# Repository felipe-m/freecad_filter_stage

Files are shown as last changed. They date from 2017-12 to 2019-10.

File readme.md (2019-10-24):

# One-axis stage to move a filter

This is a parametrizable open-source hardware (OSH) stage to move an optical filter. 
The dimensions of the filter and the stage are parametrizable in order to change the dimensions of the stage, the filter and any other components (stepper motor, belt tensioner, aluminum profiles,..)
The printable pieces are described using [FreeCAD](http://freecadweb.org/) Python scripts.
It can be compared with the OpenSCAD version: https://github.com/felipe-m/oscad_filter_stage

1. [License](#license)
2. [Description](#description)
3. [Assembly](#assembly)
4. [Main parameters](#main_parameters)
    1. [Filter Holder Parameters](#filter_holder_param)
    2. [Belt Tensioner](#belt_tensioner_param)
5.  [Project organization](#directory)
6.  [Printable Parts](#printed_parts)
    1. [Parts with step by step tutorial](#tutorial_step)
    2. [The rest of the parts](#no_tutorial)
7.  [Print settings](#print_set)

**The pictures of this readme.md are reduced in size to make the document more readable** larger pictures can be found in the img folder (see [Project organization](#directory))

---
## License 

Hardware License: CERN 1.2 (https://ohwr.org/cernohl)

Software License: [LGPL 3.0](./License.md)

Documentation License: CC BY 4.0 (https://creativecommons.org/licenses/by/4.0/)

ES000004

This project has been certified as [open source hardware](https://certification.oshwa.org/es000004.html) by the [Open Source Hardware Association](https://www.oshwa.org/). 

## Description 

The components of the stage are:
* Filter holder
* Timming belt
* Belt tensioner
* Stepper motor with pulley
* Motor holder
* Linear guide
* Some nuts and bolts

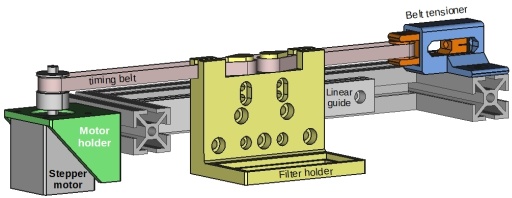
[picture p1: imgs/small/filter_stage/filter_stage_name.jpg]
Filter Stage Names


---

## Assembly 

### Filter holder

The filter holder holds an optical filter and it is attached to a linear guide. 

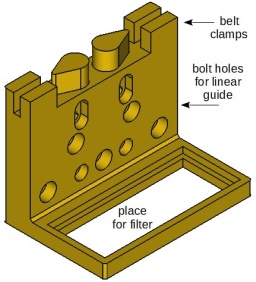
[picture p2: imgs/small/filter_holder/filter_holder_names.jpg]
Filter Holder Names


It has various holes to be able to fit in different linear guides

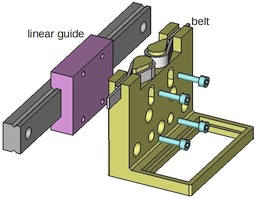
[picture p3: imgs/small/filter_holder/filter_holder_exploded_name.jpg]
Filter Holder Exploded


### Belt tensioner

The belt tensioner is composed by 2 printable parts, and idler pulley:
* Tensioner holder
* Idler tensioner
* Idler pulley
* Leadscrew with nut

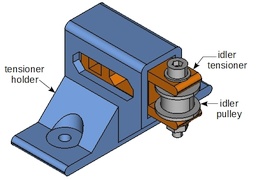
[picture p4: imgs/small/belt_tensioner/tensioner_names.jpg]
Belt tensioner front


Back view of the belt tensioner:

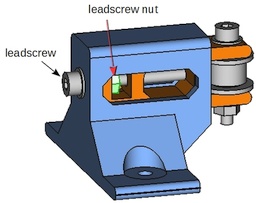
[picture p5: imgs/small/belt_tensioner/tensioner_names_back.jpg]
Belt tensioner back


Exploded view of the belt tensioner:

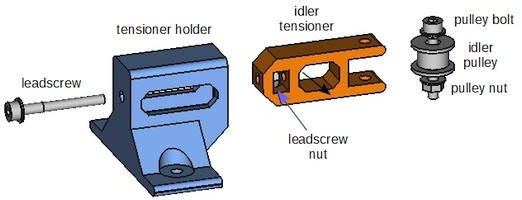
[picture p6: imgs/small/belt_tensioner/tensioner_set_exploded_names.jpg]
Belt tensioner exploded


By turning the leadscrew, the idler pulley will retract or extend, tightening or loosening the belt. 

Retracted belt tensioner:

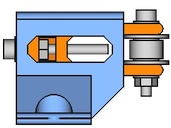
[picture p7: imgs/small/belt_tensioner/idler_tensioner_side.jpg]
Belt tensioner retracted


Extended belt tensioner:

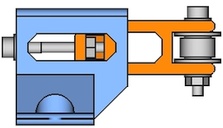
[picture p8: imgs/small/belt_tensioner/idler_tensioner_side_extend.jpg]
Belt tensioner extended


The idler pulley can be made out of a bearing, a bolt, a nut and some washers. 
For example, if using a DIN 912 bolt, it can be built this way:

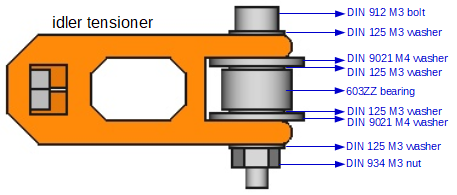
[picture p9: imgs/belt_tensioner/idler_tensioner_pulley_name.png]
Idler pulley bearing


---

## Main Parameters 
Following, the main parameters are explained.
There are some other parameters that can be seen in the Python code.

---

### Filter Holder Parameters 

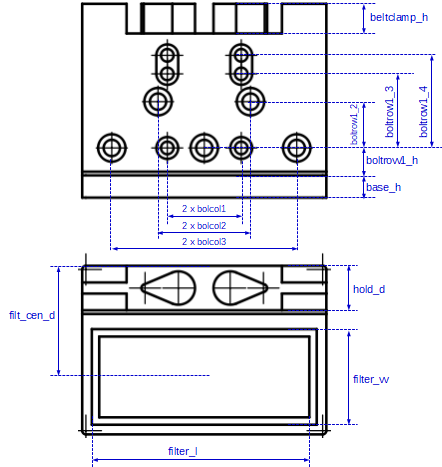
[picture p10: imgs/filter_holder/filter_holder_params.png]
Filter holder parameters


Example of 2 filter holders having different parameters:

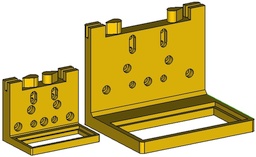
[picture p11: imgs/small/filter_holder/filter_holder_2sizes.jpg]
2 Filter holder size


---

### Belt tensioner Parameters 

Idler tensioner size depending on the idler pulley:

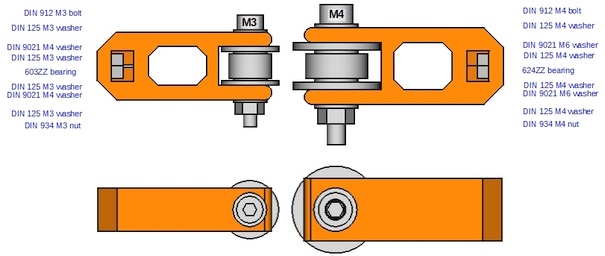
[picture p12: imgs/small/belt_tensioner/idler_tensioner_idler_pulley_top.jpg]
Idler tensioner size depending on the idler pulley


---

The tensioner stroke can be modified:

tensioner stroke

---

The thickness of the walls can be modified

tensioner wall thick

---

The metric size of the leadscrew can be modified:

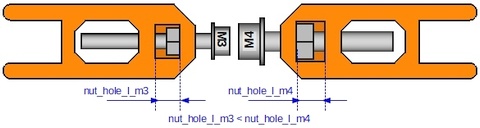
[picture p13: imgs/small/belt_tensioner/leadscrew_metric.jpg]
Leadscrew size


---

These modifications lead to automatic modifications on the tensioner holder size:

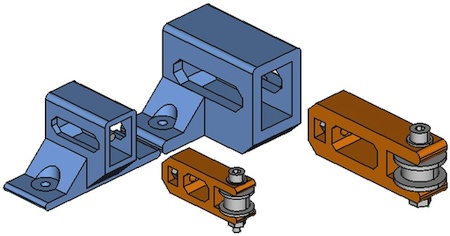
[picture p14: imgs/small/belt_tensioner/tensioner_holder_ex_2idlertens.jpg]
Tensioner holder size


---

The belt height is parametrizable, leading to modifications on the tensioner holder:

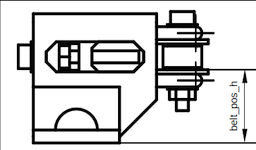
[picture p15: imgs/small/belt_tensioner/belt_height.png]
Belt height


---

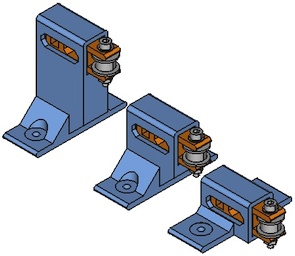
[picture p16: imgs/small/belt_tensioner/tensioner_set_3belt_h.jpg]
Belt height


---

The base width, ie. the aluminum profile width, is parametrizable:

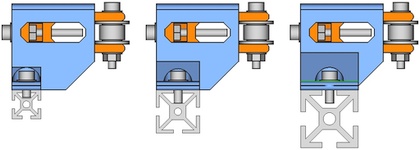
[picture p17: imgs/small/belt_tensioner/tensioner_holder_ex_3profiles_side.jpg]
Base width


---

## Project organization 
```
 +--- scr: Source files in Python
    +--- comps: functions in Python for FreeCAD, https://github.com/felipe-m/fcad-comps
 +--- scr_cq: Source files in Python using CadQuery   
 +--- freecad: Saved FreeCAD designs
 +--- stl: Parts exported to STL
 +--- imgs: Images of the 4 parts in png format
    +--- small: reduced size images
    +--- tens_hold_steps: images for the step by step explanation for the tensioer holder
    +--- idler_tens_steps: images for the step by step explanation for the idler tensioner
    +--- belt_tensioner: belt tensioner images
    +--- filter_holder: filter holder images
    +--- filter_stage: filter stage images
```

 comps: are python functions and classes to make the shapes easier. Check https://github.com/felipe-m/fcad-comps

---

## Step by step explanations :

### Step by step explanations :

1. [tensioner_holder.md](./tensioner_holder.md) Detailed explanation for the tensioner holder. It also includes information on how to execute the Python scripts. 
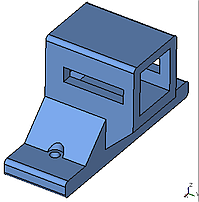
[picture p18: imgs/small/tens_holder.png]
Tensioner Holder

1. [idler_tensioner.md](./idler_tensioner.md) Detailed explanation for the idler tensioner
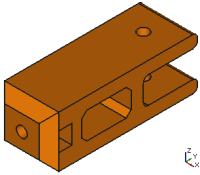
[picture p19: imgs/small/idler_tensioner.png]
Idler Tensioner


You can compare the same pieces designed using OpenSCAD: https://github.com/felipe-m/oscad_filter_stage

---

### Designs with no step by step explanations :
1. The [tensioner_set.py](src/tensioner_set.py) module has no detailed explanation, but the code is explained based on the previous. This code combines the parts of the tensioner set and uses Python classes and methods.
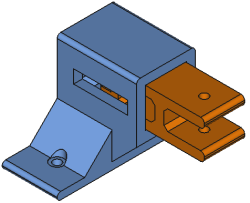
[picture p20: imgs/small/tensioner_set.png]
Tensioner Set

1. [filter_holder_clss.py](src/filter_holder_clss.py) Filter holder, similar to the one made with OpenSCAD (https://github.com/felipe-m/oscad_filter_stage)
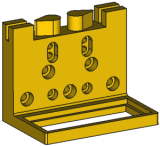
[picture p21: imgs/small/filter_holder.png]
Filter Holder

1. [filter_stage.py](src/filter_stage.py) In the same design includes the filter holder, the belt tensioner and the motor holder, and also some other non-printable models, such as the stepper motor, aluminum profile, linear guide, belt and pulleys
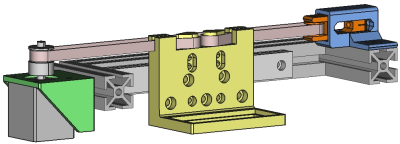
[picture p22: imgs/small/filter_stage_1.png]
Filter Stage

1. CadQuery designs have no step-by-step explanations, but there are comments in the code:
 + [cq_idler_tensioner.py](src_cq/cq_idler_tensioner.py)
 + [cq_tensioner_holder.py](src_cq/cq_tensioner_holder.py)
 + [cq_nemamotor_bracket.py](src_cq/cq_nemamotor_bracket.py)
 + [cq_filter_holder.py](src_cq/cq_filter_holder.py)
 
## Print settings :

There is no need to have supports as long as the parts are printed with the following orientation:

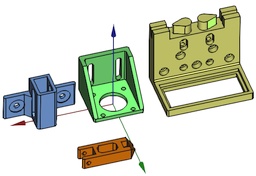
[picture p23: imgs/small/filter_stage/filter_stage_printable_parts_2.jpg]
Print orientation


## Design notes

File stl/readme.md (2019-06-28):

* [idler_tensioner.stl](idler_tensioner.stl) is the result of [idler_tensioner.py](../src/idler_tensioner.py)
* [tensioner_holder.stl](tensioner_holder.stl) is the result of [tensioner_holder.py](../src/tensioner_holder.py)
* [set_idler_tensioner.stl](set_idler_tensioner.stl) and [set_tensioner_holder.stl](set_tensioner_holder.stl) are the result of [tensioner_set.py](../src/tensioner_set.py)
* [class_idler_tensioner.stl](class_idler_tensioner.stl) and [class_tensioner_holder.stl](class_tensioner_holder.stl) are the result of [tensioner_clss.py](../src/tensioner_clss.py) used in the [filter stage example](../src/filter_stage.py).
* [filter_holder.stl](filter_holder.stl) is the result of [filter_holder_clss.py](../src/filter_holder_clss_clss.py) used in the [filter stage example](../src/filter_stage.py).
* [motor_holder.stl](motor_holder.stl) is a part of the same [filter stage example](../src/filter_stage.py).

---

## Print orientation

This sample parts are from the [filter stage example](../src/filter_stage.py).

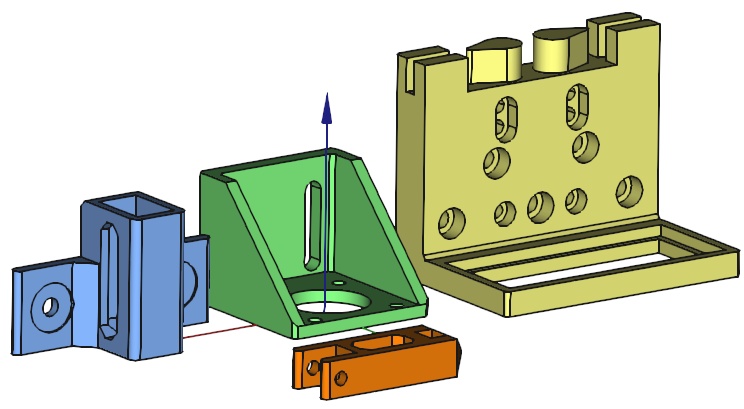
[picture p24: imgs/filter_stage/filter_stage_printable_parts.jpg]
Print orientation


---

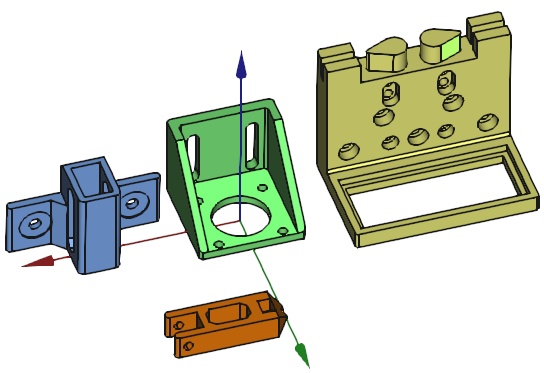
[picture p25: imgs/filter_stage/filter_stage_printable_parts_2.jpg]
Print orientation 2


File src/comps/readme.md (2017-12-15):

# FreeCAD scripted components and functions

## `kcomp.py`

Constants and dimensions for components:
* LME10UU, LME12UU linear bearing
* E3D V6 extruder
* DIN-912 bolt
* DIN-934 nut
* SK12 shaft holder

It also includes the default tolerances and the 3D printer layer height

## `comps.py`

Creates freecad components

### Dependencies:
../fcfun functions
/../../freecad/comps/misumi_profile_hfs_serie6_w8_30x30.FCStd

### Components

**class Sk**

SK12 shaft holder

**class MisumiAlu30s6w8**

Misumi Aluminum extrusion 30x30 hfs serie 6 width 8

## `fcfunc.py`

Python functions and constants for FreeCAD scripts

```
def addBox (x, y, z, name, cx= False, cy=False)
def addCyl (r, h, name)
def addBolt (r_shank, l_bolt, r_head, l_head,
             hex_head = 0, extra=1, support=1, headdown = 1, name="bolt")
def addBoltNut_hole (r_shank,        l_bolt, 
                     r_head,         l_head,
                     r_nut,          l_nut,
                     hex_head = 0,   extra=1,
                     supp_head=1,    supp_nut=1,
                     headdown=1,     name="bolt")         
class NutHole ()
    def __init__(self, nut_r, nut_h, hole_h, name,
                 extra = 1, nuthole_x = 1, cx=0, cy=0, holedown = 0)            
def fillet_len (box, e_len, radius, name)            
```

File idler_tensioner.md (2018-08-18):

# FreeCAD python scripts detailed steps for the Idler Tensioner

Idler Tensioner

This example is created using python functions defined in the folder src/comps

The source file: [idler_tensioner.py](src/idler_tensioner.py)

The resulting FreeCAD model: [idler_tensioner.FCStd](freecad/idler_tensioner.FCStd)

This tutorial can be compared with the [OpenSCAD tutorial](https://github.com/felipe-m/oscad_filter_stage) for this [Idler Tensioner](https://github.com/felipe-m/oscad_filter_stage/blob/master/idler_tensioner.md) 

With FreeCAD you can navigate through the model:

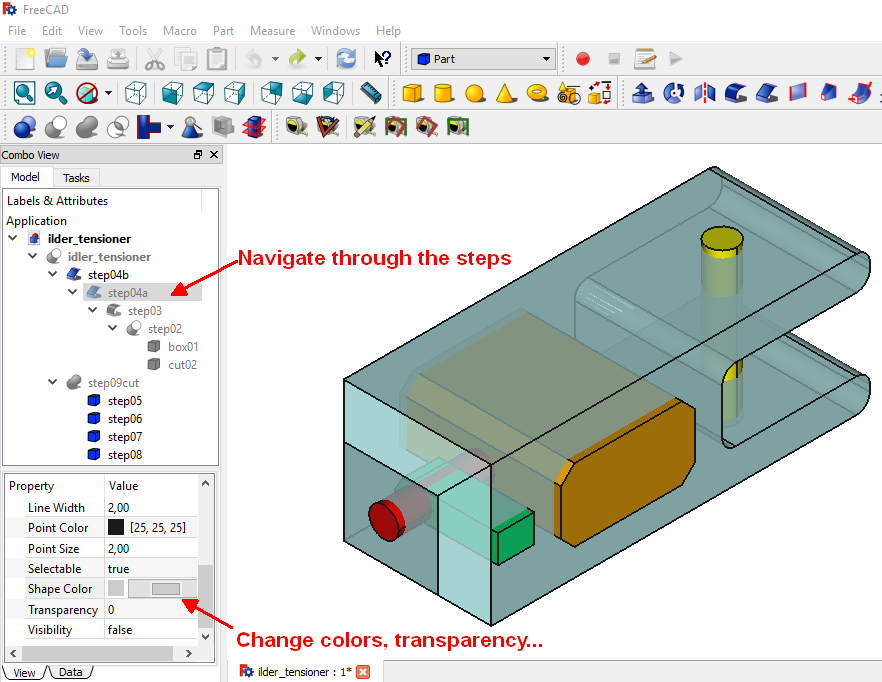
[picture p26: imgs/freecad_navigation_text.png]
Navigate


You may want to check the steps for the [tensioner holder](./tensioner_holder.md), which have been also created using Python scripts, but using other kind of functions

Back to the [readme.md](./readme.md)

# Steps

## Step 00: Libraries import and function creation

```python
import os
import sys
import FreeCAD
import FreeCADGui
import Part

# to get the current directory. Freecad has to be executed from the same
# directory this file is
filepath = os.getcwd()
# to get the components
# In FreeCAD can be added: Preferences->General->Macro->Macro path
sys.path.append(filepath) 
#sys.path.append(filepath + '/' + 'comps')
sys.path.append(filepath + '/../../' + 'comps')

import kcomp   # import material constants and other constants
import fcfun   # import my functions for freecad. FreeCad Functions
import comps   # import my CAD components
import partgroup   # import my CAD components
import kidler  # import constants for the idler tensioner and holder
import kparts

def idler_tens ():
    # bring the active document
    doc = FreeCAD.ActiveDocument
```

## Step 01: Create the box
Everything else will cut the box:

```python
    #  --------------- step 01 ---------------------------      
    #  rectangular cuboid with basic dimensions
    # 
    #           Z
    #           :.....tens_l.......
    #           :_________________:
    #           /                /|
    #          /                / |
    #       ../________________/  |..............Y     .
    #      :  |                |  /     . 
    # tens_h  |                | /     . tens_w
    #       :.|________________|/......
    #        .
    #       .
    #      X 
    #
    # oscad: cube([tens_w, tens_l, tens_h]);

    # creates the shape, you don't see it yet on FreeCAD Gui
    shp01 = fcfun.shp_boxcen(kidler.tens_w, kidler.tens_l, kidler.tens_h)
    # creates a freecad object from the shape, to see it in FreeCAD Gui,
    # not necessary, but illustrative for this tutorial
    fcd01 = fcfun.add_fcobj(shp01, 'box01')

```

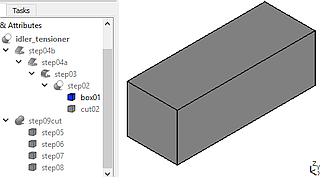
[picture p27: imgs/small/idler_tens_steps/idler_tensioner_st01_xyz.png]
Step 01


## Step 02: Space for the idler pulley

```python
    #  --------------- step 02 ---------------------------  
    # Space for the idler pulley
    #      Z
    #      :
    #      :_______________________
    #      |                 ______|....
    #      |                /          + idler_h
    #      |               |           :
    #      |                \______....:
    #      |_______________________|...wall_thick.......> Y
    #                      :       :
    #                      :.......:
    #                         +
    #                       2 * idler_r_xtr
    #
    # oscad: translate ([-1, tens_l - 2*idler_r_xtr, wall_thick])
    # ...
    pos02 = FreeCAD.Vector(-1,
                           kidler.tens_l - 2*kidler.idler_r_xtr,
                           kidler.wall_thick)
    # oscad: cube([tens_w+2, 2 * idler_r_xtr +1, idler_h]);
    # ...
    # creates the shape already filleted on X, make it larger on Y to make 
    # the chamfer easier, so all X edges are chamfered, but since is larger
    # on Y, it doesnt matter.  y dimensions
    shp02cut = fcfun.shp_boxcenfill(
                     x = kidler.tens_w+2,
                     # in_fillet added
                     y = 2 * kidler.idler_r_xtr +1 + kidler.in_fillet,
                     z = kidler.idler_h,
                     fillrad = kidler.in_fillet,
                     fx = True, fy = False, fz = False, # chamfer on X
                     pos = pos02)
    fcd02cut = fcfun.add_fcobj(shp02cut, 'cut02')
    # difference (cut) of fcd01 and fcd02cut
    fcd02 = doc.addObject("Part::Cut", 'step02')
    fcd02.Base = fcd01
    fcd02.Tool = fcd02cut
    # the shape
    shp02 = fcd02.Shape

    doc.recompute()
```
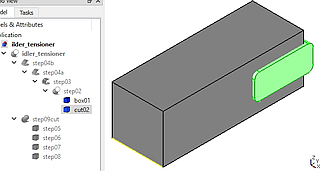
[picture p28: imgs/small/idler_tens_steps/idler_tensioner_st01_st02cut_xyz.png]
Step 02

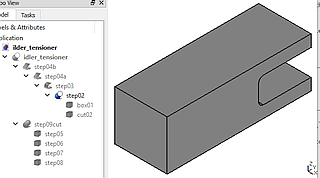
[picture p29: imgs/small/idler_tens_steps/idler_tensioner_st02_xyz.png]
Step 02


## Step 03: Fillets at the idler end

```python
    # Fillets at the idler end:

    #      Z
    #      :
    #      :_______________________f2
    #      |                 ______|
    #      |                /      f4
    #      |               |
    #      |                \______f3...
    #      |_______________________|....+ wall_thick.....> Y
    #      :                       f1
    #      :...... tens_l .........:
    #
    fcd03 = fcfun.filletchamfer (fcd02, e_len = kidler.tens_w,
                                name = 'step03',
                                fillet = 1,
                                radius = kidler.in_fillet,
                                axis = 'x',  # axis to fillet
                                ypos_chk = 1,
                                ypos = kidler.tens_l) #fillet on y=tens_l

```
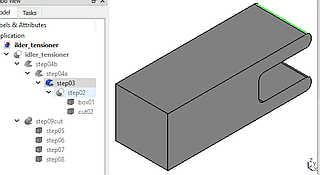
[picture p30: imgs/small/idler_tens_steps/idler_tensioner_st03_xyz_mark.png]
Step 03


## Step 04: Chamfers at the nut end

```python
    #  --------------- step 04 --------------------------- 
    # Chamfers at the nut end:

    #      Z
    #      :
    #      : ______________________
    #    ch2/                ______|
    #      |                /             
    #      |               |        
    #      |                \______
    #    ch1\______________________|.............> Y
    #      :                       :
    #      :...... tens_l .........:
    # 
    fcd04a = fcfun.filletchamfer (fcd03, e_len = 0,
                                  name = 'step04a',
                                  fillet = 0,  # chamfer
                                  radius = 2* kidler.in_fillet,
                                  axis = 'x',  # axis to fillet
                                  ypos_chk = 1,
                                  ypos = 0) #fillet on y=0

```
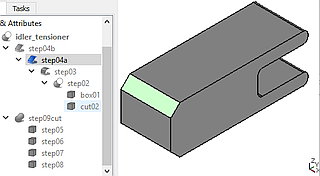
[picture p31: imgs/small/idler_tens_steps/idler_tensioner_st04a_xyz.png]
Step 04a


## Step 04 Optional: Chamfers at the nut end on axis Z
They are 45 degrees so they should print ok without support, but you may
not want to have them

```python
   #  --------------- step 04b OPTIONAL---------------------- 
   #  Chamfers at the nut end on axis Z, they are 45 degrees
   #  so they should print ok without support, but you may
   #  not want to have them

   #        ________ ....> X
   #    ch1/________\ch2
   #       |        |
   #       |        |
   #       |        |
   #       |        |
   #       |        |
   #       |        |
   #       |........|
   #       |        |
   #       |        |
   #       |        |
   #       |________|
   #       :
   #       Y
   #       
   # 

    if (kidler.opt_tens_chmf == 1) : # optional tensioner chamfer
        fcd04 = fcfun.filletchamfer (fcd04a, e_len = 0,
                                      name = 'step04b',
                                      fillet = 0,  # chamfer
                                      radius = 2* kidler.in_fillet,
                                      axis = 'z',  # axis to fillet
                                      ypos_chk = 1,
                                      ypos = 0) #fillet on y=0
    else:
        # just to have the same freecad object at the end of step 4 in fcd04
        fcd04 = fcd04a 

```

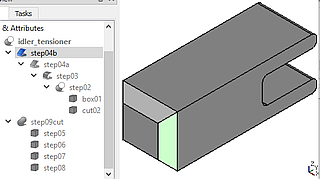
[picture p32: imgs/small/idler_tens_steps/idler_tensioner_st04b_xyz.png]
Step 04b


## Step 05: Shank hole for the idler pulley

```python
    #  --------------- step 05 --------------------------- 
    # Shank hole for the idler pulley:

    #      Z                     idler_r_xtr
    #      :                    .+..
    #      : ___________________:__:
    #       /                __:_:_|
    #      |                /             
    #      |               |        
    #      |                \______
    #       \__________________:_:_|.............> Y
    #      :                       :
    #      :...... tens_l .........:
    #                     
    #oscad: translate ([tens_w/2., tens_l - idler_r_xtr, -1])
    #oscad:     cylinder (r=boltidler_r_tol, h= tens_w +2, $fa=1, $fs=0.5);
    pos05 = FreeCAD.Vector(kidler.tens_w/2.,
                           kidler.tens_l - kidler.idler_r_xtr,
                           -1)
    fcd05 = fcfun.addCylPos (r = kidler.boltidler_r_tol,
                             h = kidler.tens_h +2,
                             name = 'step05',
                             pos = pos05)
    # we will make the cut at the end with the other cuts
```

Step05 is the yellow cylinder:

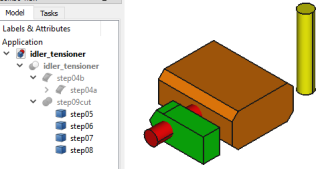
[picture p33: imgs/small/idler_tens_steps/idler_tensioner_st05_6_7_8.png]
Step 05

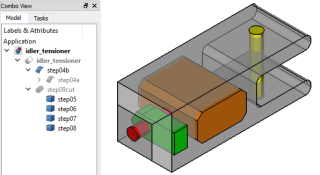
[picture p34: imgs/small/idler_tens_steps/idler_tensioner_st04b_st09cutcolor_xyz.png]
Step 05
  

## Step 06: Hole for the leadscrew (stroke)

```python
    #  --------------- step 06 --------------------------- 
    # Hole for the leadscrew (stroke):

    #      Z
    #      :
    #      : ______________________
    #       /      _____     __:_:_|
    #      |    f2/     \f4 /             
    #      |     |       | |        
    #      |    f1\_____/f3 \______
    #       \__________________:_:_|.............> Y
    #      :     :       :         :
    #      :     :.......:         :
    #      :     :   +             :
    #      :.....:  tens_stroke    :
    #      :  +                    :
    #      : nut_holder_total      :
    #      :                       :
    #      :...... tens_l .........:
    # 

    #  Space for screw (the stroke)
    #oscad: translate ([-1, nut_holder_total,wall_thick])
    pos06 = FreeCAD.Vector (-1,
                            kidler.nut_holder_total,
                            kidler.wall_thick)
    # shape of a box with fillet in all the X edges
    #oscad: cube([tens_w+2, tens_stroke, idler_h]);
    shp06 = fcfun.shp_boxcenchmf (x = kidler.tens_w+2,
                                  y = kidler.tens_stroke,
                                  z = kidler.idler_h,
                                  chmfrad = kidler.in_fillet,
                                  fx = True,
                                  fz = False,
                                  pos = pos06)
    fcd06 = fcfun.add_fcobj(shp06, 'step06')

```

Step06 is the orange element

Step 06
  Step 06

## Step 07: Hole for the leadscrew shank at the beginning

```python
    #  --------------- step 07 --------------------------- 
    # Hole for the leadscrew shank at the beginning

    #      Z
    #      :
    #      : ______________________
    #       /      _____     __:_:_|
    #      |      /     \   /
    #      |:::::|       | |
    #      |      \_____/   \______
    #       \__________________:_:_|.............> Y
    #      :     :                 :
    #      :     :                 :
    #      :     :                 :
    #      :.....:                 :
    #      :  +                    :
    #      : nut_holder_total      :
    #      :                       :
    #      :...... tens_l .........:
    #                       
    #oscad: translate ([tens_w/2, -1, tens_h/2])
    pos07 = FreeCAD.Vector(kidler.tens_w/2,
                           -1,
                           kidler.tens_h/2)
    #oscad:rotate ([-90,0,0])
    #oscad: cylinder (r=bolttens_r_tol, h=nut_holder_total+2,$fa=1, $fs=0.5);
    fcd07 = fcfun.addCylPos (r = kidler.bolttens_r_tol,
                             h = kidler.nut_holder_total +2.,
                             name = 'step07',
                             normal = fcfun.VY, #on the positive y axis
                             pos = pos07)
```
Step07 is the red cylinder

Step 07
  Step 07

## Step 08: Hole for the leadscrew nut

```python
    #  --------------- step 08 --------------------------- 
    # Hole for the leadscrew nut

    #      Z
    #      :
    #      : ______________________
    #       /      _____     __:_:_|
    #      |  _   /     \   /
    #      |:|_|:|       | |
    #      |      \_____/   \______
    #       \__________________:_:_|.............> Y
    #      : :   :                 :
    #      :+    :                 :
    #      :nut_holder_thick       :
    #      :.....:                 :
    #      :  +                    :
    #      : nut_holder_total      :
    #      :                       :
    #      :...... tens_l .........:
    #                       

    #oscad: tens_w/2-1 to have more tolerance, so it is a little bit deeper
    #oscad: translate ([tens_w/2-1, nut_holder_thick, tens_h/2])
    # dont need to have tens_w/2-1, because there is xtr argument for that
    pos08 = FreeCAD.Vector (kidler.tens_w/2., 
                            kidler.nut_holder_thick,
                            kidler.tens_h/2.)
    #oscad: cylinder (r=m4_nut_r_tol+stol, h = nut_space, $fn=6);
    #oscad:  cube([tens_w/2 + 2, nut_space, 2*m4_nut_ap_tol]);
    shp08 = fcfun.shp_nuthole (nut_r = kidler.tensnut_circ_r_tol,
                               nut_h = kidler.nut_space,
                               hole_h = kidler.tens_w/2,
                               xtr_nut = 1, xtr_hole = 1, 
                               # on the Y direction
                               fc_axis_nut = FreeCAD.Vector(0,1,0),
                               # on the X direction
                               fc_axis_hole = FreeCAD.Vector(1,0,0),
                               ref_nut_ax = 2, # pos not centered on axis nut 
                               # pos at center of nut on axis hole 
                               ref_hole_ax = 1, 
                               pos = pos08)
    fcd08 = fcfun.add_fcobj(shp08, 'step08')
```

Step08 is the green element:

Step 08
  Step 08

## Step 09: Union of all the elements to cut, and final cut
```python
    # --------- step 09:
    # --------- Last step, union and cut of the steps 05, 06, 07, 08
    fcd09cut = doc.addObject("Part::MultiFuse", "step09cut")
    fcd09cut.Shapes = [fcd05,fcd06,fcd07,fcd08]
    fcd09final = doc.addObject("Part::Cut", "idler_tensioner")
    fcd09final.Base = fcd04
    fcd09final.Tool = fcd09cut
    doc.recompute()
    return fcd09final
```
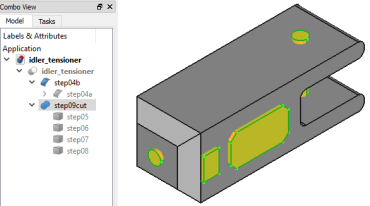
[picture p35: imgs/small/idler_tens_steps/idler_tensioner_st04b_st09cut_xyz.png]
Idler Tensioner

Idler Tensioner

## Step 10: Saving, rotating to print and export:

```python
# creation of a new FreeCAD document
doc = FreeCAD.newDocument()
# creation of the idler tensioner
fcd_idler_tens = idler_tens()
# change color to orange:
fcd_idler_tens.ViewObject.ShapeColor = (1.0, 0.5, 0.0)

# ---------- export to stl
stlPath = filepath + '/../stl/'
stlFileName = stlPath + 'ilder_tensioner' + '.stl'
# rotate to print without support:
fcd_idler_tens.Placement.Rotation = (
                    FreeCAD.Rotation(FreeCAD.Vector(0,1,0), -90))
# exportStl is not working well with FreeCAD 0.17 (worked on 0.16 and 0.15)
#fcd_idler_tens.Shape.exportStl(stlFileName)
mesh_shp = MeshPart.meshFromShape(fcd_idler_tens.Shape,
                                  LinearDeflection=kparts.LIN_DEFL, 
                                  AngularDeflection=kparts.ANG_DEFL)
mesh_shp.write(stlFileName)
del mesh_shp

# rotate back
fcd_idler_tens.Placement.Rotation = (
                    FreeCAD.Rotation(FreeCAD.Vector(1,0,0), 0))

# save the FreeCAD file
freecadPath = filepath + '/../freecad/'
freecadFileName = freecadPath + 'ilder_tensioner' + '.FCStd'
doc.saveAs (freecadFileName)
```

Idler tensioner rotated to be exported to stl and print:

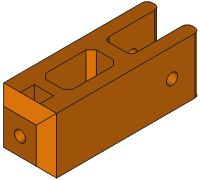
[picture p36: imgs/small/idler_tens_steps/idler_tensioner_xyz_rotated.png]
Idler Tensioner


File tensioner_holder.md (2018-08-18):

# FreeCAD python scripts detailed steps for the Tensioner Holder

Tensioner Holder

This example is created using FreeCAD python functions and all objects are created using objects in the FreeCAD document.

Check [the FreeCAD scripting basics tutorial](https://www.freecadweb.org/wiki/FreeCAD_Scripting_Basics) for more information

The source file: [tensioner_holder.py](src/tensioner_holder.py)

The resulting FreeCAD model: [tensioner_holder.FCStd](freecad/tensioner_holder.FCStd)

This tutorial can be compared with the [OpenSCAD tutorial](https://github.com/felipe-m/oscad_filter_stage) for this [Tensioner Holder](https://github.com/felipe-m/oscad_filter_stage/blob/master/tensioner_holder.md) 

## Running python scripts

If you run the Python script, make sure to read this tutorial: https://www.freecadweb.org/wiki/Python_scripting_tutorial.

Go to **Edit->Prefences->General->Output window** and check 2 boxes:

- Redirect internal Python output to report view
- Redirect internal Python errors to report view

Then go to **View->Panels** and check:

- Report view

Also, for this script, go to: **Edit->Preferences->PartDesign** to enable automatic checking and refining of the model after Boolean and sketch based operations (performance may be affected if these options are left switched on). 

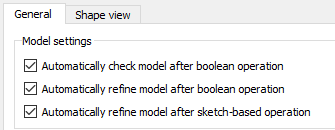
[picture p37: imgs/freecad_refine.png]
FreeCAD automatic refine


## Python scripting in FreeCAD

Using Python scripts in FreeCAD to make your own CAD models can be done in many different ways.

This example is created using FreeCAD python functions and all objects are created using Objects.

On the other example, functions to create shapes were used:  [idler tensioner](./idler_tensioner.md)

Back to the [readme.md](./readme.md)

## Steps

### Step 00: Libraries import and function creation

```python
import os
import sys
import FreeCAD
import FreeCADGui
import Part

# to get the current directory. Freecad has to be executed from the same
# directory this file is
filepath = os.getcwd()
# to get the components
# In FreeCAD can be added: Preferences->General->Macro->Macro path
sys.path.append(filepath) 
#sys.path.append(filepath + '/' + 'comps')
sys.path.append(filepath + '/../../' + 'comps')

import kidler  # import constants for the idler tensioner and holder
import kparts

# to make a comparision of equality in floats, less than this number
mindif = 0.001

def tensioner_holder():
    # bring the active document
    doc = FreeCAD.ActiveDocument
```

## Step 01: Create the base

```python
    #  --------------- step 01 ---------------------------      
    #    the base, to attach it to the aluminum profiles
    #    
    #
    #                                           Z      Z
    #                                           :      :
    #                 .. _______________________:      :________
    #     hold_bas_h.+..|_______________________|      |________|......Y
    #
    #                    .... hold_bas_w ........
    #                   :                        :
    #            X......:________________________:....
    #                   |                        |    :
    #                   |                        |    + hold_bas_l
    #                   |________________________|....:
    #                                            :
    #                                            Y
    #
    # cube([hold_bas_w, hold_bas_l, hold_bas_h]);
    fcd01 = doc.addObject("Part::Box",'base_box_st01')
    fcd01.Length = kidler.hold_bas_w
    fcd01.Width = kidler.hold_bas_l
    fcd01.Height = kidler.hold_bas_h
```

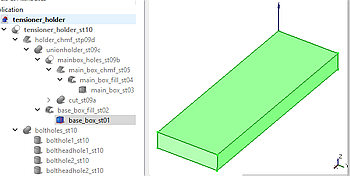
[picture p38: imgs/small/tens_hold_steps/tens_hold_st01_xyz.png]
Step 01


## Step 02: Fillet the base

```python
   #    --------------- step 02 --------------------------- 
    #    Fillet the base
    #    The piece will be printed on the XZ plane, so this fillet will be 
    #    raising
    #  
    #                                         Z
    #                                         :
    #                f4_______________________f2
    #          X......(_______________________)
    #                f3                        f1
    #
    edgefill_list = []
    # for each edge, take the 2 vertexes:
    for edge_ind, edge in enumerate(fcd01.Shape.Edges):
        v0 = edge.Vertexes[0]
        v1 = edge.Vertexes[1]
        # check if this 2 Vertexes have the same X, Z: so they are the Y axis
        # since they are floats, would be better to compare within a range
        #if abs(v0.X-v1.X) < mindif  and abs(v0.Z - v1.Z) < mindif: 
        if v0.X == v1.X and v0.Z == v1.Z: 
            edgefill_list.append((edge_ind+1, # numbered starting in 1
                                  kidler.in_fillet, kidler.in_fillet))
    fcd02 = doc.addObject ("Part::Fillet", 'base_box_fill_st02')
    fcd02.Base = fcd01
    fcd02.Edges = edgefill_list
    # It is recomended to recompute after fillet/chamfer and other operations
    doc.recompute()
    # hide the step 01:
    fcd01.ViewObject.Visibility = False
```
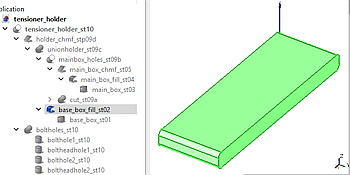
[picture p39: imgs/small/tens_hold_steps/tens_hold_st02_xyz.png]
Step 02


## Step 03: The main box

```python
    #    --------------- step 03 --------------------------- 
    #    The main box
    #                             aluprof_w   Z      Z
    #                                  ..+....:      :
    #           .............. _______:       :      :____________
    #           :             |       |       :      |            |
    #           :             |       |       :      |            |
    #   hold_h +:             |       |       :      |            |
    #           :             |       |       :      |            |     
    #           :      _______|       |_______:      |________    |
    #       X...:.....(_______|_______|_______)      |________|___|...Y
    #                                                :            :
    #                  .... hold_bas_w ........      :.. hold_l...:
    #                 :                        :
    #                 :        .hold_w.        :
    #                 :       :       :        :
    #          X......:_______:_______:________:....
    #                 |       |       |        |    :
    #                 |       |       |        |    + hold_bas_l
    #                 |_______|       |________|....:
    #                         |       |        :
    #                         |_______|        :
    #                                          :
    #                                          :
    #                                          Y
    #oscad: translate ([aluprof_w,0,0])
    #oscad    cube([hold_w, hold_l, hold_h]);
    fcd03 = doc.addObject("Part::Box",'main_box_st03')
    fcd03.Length = kidler.hold_w
    fcd03.Width = kidler.hold_l
    fcd03.Height = kidler.hold_h
    fcd03.Placement.Base = FreeCAD.Vector(kidler.aluprof_w, 0,0)

```
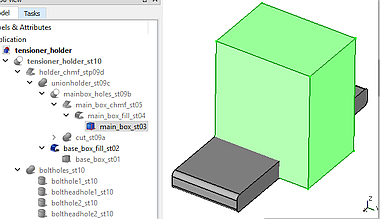
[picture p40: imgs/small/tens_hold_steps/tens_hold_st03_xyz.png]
Step 03


## Step 04: Fillets on top

```python
    #    --------------- step 04 --------------------------- 
    #    Fillets on top
    #                             aluprof_w   Z
    #                                  ..+....:
    #           .............f2_______f1      : 
    #           :             /       \       :
    #           :             |       |       :
    #   hold_h +:             |       |       :
    #           :             |       |       :
    #           :      _______|       |_______:
    #       X...:.....(_______|_______|_______)
    #
    edgefill_list = []
    # for each edge, take the 2 vertexes:
    for edge_ind, edge in enumerate(fcd03.Shape.Edges):
        v0 = edge.Vertexes[0]
        v1 = edge.Vertexes[1]
        # check if this 2 Vertexes have the same Z and is equal to hold_h
        # and their X are the same
        # again, better to use range differences: 
        if (abs(v0.Z-kidler.hold_h) < mindif and
            abs(v1.Z-kidler.hold_h) < mindif and 
            abs(v0.X - v1.X) < mindif) : 
        #if (v0.Z == kidler.hold_h and
        #    v1.Z == kidler.hold_h and
        #    v0.X == v1.X) : 
            edgefill_list.append((edge_ind+1, # numbered starting in 1
                                  kidler.in_fillet, kidler.in_fillet))
    fcd04 = doc.addObject ("Part::Fillet", 'main_box_fill_st04')
    fcd04.Base = fcd03
    fcd04.Edges = edgefill_list
    doc.recompute()
    # hide the step 03:
    fcd03.ViewObject.Visibility = False
```
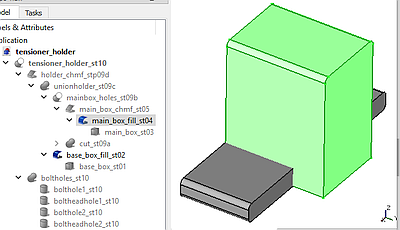
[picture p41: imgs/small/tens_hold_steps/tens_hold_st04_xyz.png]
Step 04


## Step 05: Large chamfer at the bottom

```python
   #    --------------- step 05 --------------------------- 
    #    large chamfer at the bottom

    #                                         Z      Z
    #                                         :      :
    #   Option A               _______        :      :____________
    #                         /       \       :      |            |
    #                         |       |       :      |            |
    #                         |_______|       :      |            |
    #                         |       |       :      |           /       
    #                  _______|_______|_______:      |________ /  
    #       X.........(_______________________)      |________|.......Y
    #                                                :            :

    #   
    #                                         Z      Z
    #                                         :      :
    #   Option B               _______        :      :____________
    #                         /       \       :      |            |
    #                         |       |       :      |            |
    #                         |       |       :      |            |
    #                         |_______|       :      |            |      
    #                  _______|       |_______:      |________   /  
    #       X.........(_______|_______|_______)      |________|/......Y
    #                                                :            :
    #                                                               
    edgechmf_list = []
    # option B: using more material (probably sturdier)
    chmf_rad = min(kidler.hold_l - kidler.hold_bas_l,
                   kidler.hold_h - (kidler.tens_h+2*kidler.wall_thick))
    # option A: using less material
    chmf_rad = min(kidler.hold_l-kidler.hold_bas_l+ kidler.hold_bas_h,
                   kidler.hold_h - (kidler.tens_h+2*kidler.wall_thick))
    for edge_ind, edge in enumerate(fcd04.Shape.Edges):
        v0 = edge.Vertexes[0]
        v1 = edge.Vertexes[1]
        # check if this 2 Vertexes have the same Z and is equal to 0
        # and same Y, and equal to hold_l
        # again, better to use range differences: 
        if (abs(v0.Z) < mindif and
            abs(v1.Z) < mindif and 
            abs(v0.Y - kidler.hold_l) < mindif and
            abs(v1.Y - kidler.hold_l) < mindif ):
            edgechmf_list.append((edge_ind+1, # numbered starting in 1
                                  chmf_rad, chmf_rad))
            break # there is only one
    fcd05 = doc.addObject ("Part::Chamfer", 'main_box_chmf_st05')
    fcd05.Base = fcd04
    fcd05.Edges = edgechmf_list
    doc.recompute()
    # hide the step 04:
    fcd04.ViewObject.Visibility = False
```

Option A:

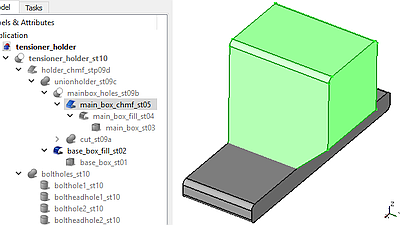
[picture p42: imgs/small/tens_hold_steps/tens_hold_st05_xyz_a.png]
Step 05a


## Step 06: Hole for the tensioner

```python
    #    --------------- step 06 --------------------------- 
    #    Hole for the tensioner
    #                                         Z      Z
    #                                         :      :
    #                          _______        :      :____________
    #                         /  ___  \       :      |c2..........|
    #                         | |   | |       :      | :          |
    #                         | |___| |       :      |c1..........|
    #                         |_______|       :      |            |      
    #                  _______|       |_______:      |________   /  
    #       X.........(_______|_______|_______)      |________|/......Y

    #
    #oscad:translate([wall_thick-tol/2, hold_l-tens_l_inside,tens_pos_h-tol/2])
    #  oscad: cube([tens_w_tol, tens_l_inside+1, tens_h_tol]);
    fcd06 = doc.addObject("Part::Box",'tens_hole_st06')
    fcd06.Length = kidler.tens_w_tol
    fcd06.Width = kidler.tens_l_inside+1
    fcd06.Height = kidler.tens_h_tol
    fcd06.Placement.Base = (  fcd03.Placement.Base 
                            + FreeCAD.Vector(kidler.wall_thick-kidler.TOL/2.,
                                             kidler.hold_l-kidler.tens_l_inside,
                                             kidler.tens_pos_h-kidler.TOL/2.))

    # chamfer:
    edgechmf_list = []
    for edge_ind, edge in enumerate(fcd06.Shape.Edges):
        v0 = edge.Vertexes[0]
        v1 = edge.Vertexes[1]
        # check if these 2 Vertexes have Y = 0 (optional chamfers)
        # and if Z are equal we only select the 2 edges (not the optional)
        if (abs(v0.Y -fcd06.Placement.Base.y) < mindif and
            abs(v1.Y -fcd06.Placement.Base.y) < mindif) :
            if (abs(v0.Z -v1.Z) < mindif  or
                kidler.opt_tens_chmf == 1):
                edgechmf_list.append((edge_ind+1, # numbered starting in 1
                                      2*kidler.in_fillet-kidler.TOL,
                                      2*kidler.in_fillet-kidler.TOL))
    fcd06chmf = doc.addObject ("Part::Chamfer", 'tens_hole_chmf_st06')
    fcd06chmf.Base = fcd06
    fcd06chmf.Edges = edgechmf_list
    doc.recompute()
    # hide the step 06:
    fcd06.ViewObject.Visibility = False
    fcd06chmf.ViewObject.ShapeColor = (1., 1., 0.) # YELLOW
```

Including optional chamfers:

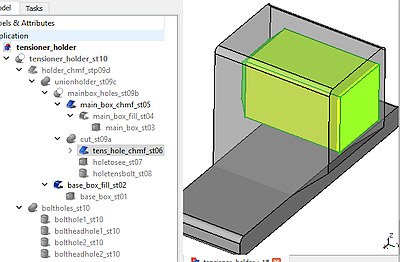
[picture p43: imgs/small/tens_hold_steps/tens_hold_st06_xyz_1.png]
Step 06

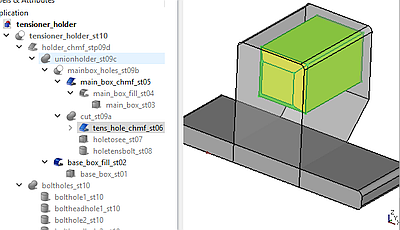
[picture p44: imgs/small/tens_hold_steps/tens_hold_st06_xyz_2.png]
Step 06
  

## Step 07: A hole to be able to see inside, could be on one side or both

```python
    #    A hole to be able to see inside, could be on one side or both
    #                                         Z      Z
    #                                         :      :
    #                          _______        :      :____________
    #                         /  ___  \       :      |  ._______ .|
    #                         |:|   |:|       :      | :|_______| |
    #                         | |___| |       :      |  ..........|
    #                         |_______|       :      |            |      
    #                  _______|       |_______:      |________   /  
    #       X.........(_______|_______|_______)      |________|/......Y

    fcd07 = doc.addObject("Part::Box",'holetosee_st07')
    if kidler.hold_hole_2sides == 1:
        fcd07.Length = kidler.hold_w+2
        fcd07_pos_x = -1
    else:
        fcd07.Length = kidler.wall_thick+2
        fcd07_pos_x =  kidler.hold_w - kidler.wall_thick-1 
    fcd07.Width = kidler.hold_l - kidler.nut_holder_thick - 2* kidler.wall_thick
    fcd07.Height = 2* kidler.tensnut_ap_tol

    # The placement will be the sum of these 2 vectors:
    #   1. placement of the main box
    #   2. relative position inside the main box
    fcd07.Placement.Base = (  fcd03.Placement.Base # main box
                            + FreeCAD.Vector(
                                   fcd07_pos_x,
                                   kidler.wall_thick + kidler.nut_holder_thick,
                                   kidler.tens_pos_h +  kidler.tens_h /2
                                     - kidler.tensnut_ap_tol)) 
    fcd07.ViewObject.ShapeColor = (0., 1., 0.) # GREEN

```

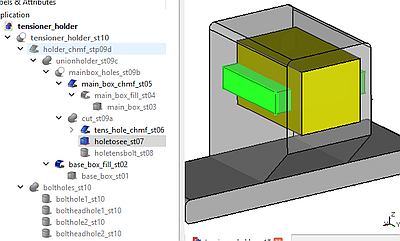
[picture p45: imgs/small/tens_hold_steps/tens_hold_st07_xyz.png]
Step 07

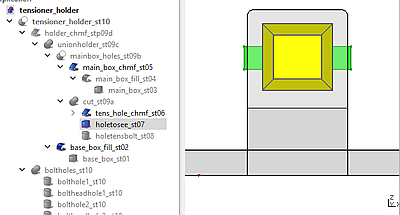
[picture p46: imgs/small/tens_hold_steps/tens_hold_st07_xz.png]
Step 07


## Step 08: Hole for the leadscrew

```python
    #    A hole for the leadscrew
    #                                         Z      Z
    #                                         :      :
    #                          _______        :      :____________
    #                         /  ___  \       :      |  ._______ .|
    #                         |:| O |:|       :      |::|_______| |
    #                         | |___| |       :      |  ..........|
    #                         |_______|       :      |            |      
    #                  _______|       |_______:      |________   /  
    #       X.........(_______|_______|_______)      |________|/......Y
    #
    #oscad: translate ([hold_w/2, -1, tens_pos_h + tens_h/2])
    #oscad:  rotate ([-90,0,0])
    #oscad:   cylinder (r=bolttens_r_tol, h=wall_thick+2, $fa=1, $fs=0.5); 
    fcd08 =  doc.addObject("Part::Cylinder",'holetensbolt_st08')
    fcd08.Radius = kidler.bolttens_r_tol
    fcd08.Height = kidler.wall_thick + 2.
    fcd08.Placement.Base = (  fcd03.Placement.Base #main box
                            + FreeCAD.Vector(
                                    kidler.hold_w/2.,
                                    -1, 
                                    kidler.tens_pos_h + kidler.tens_h/2.))
    fcd08.Placement.Rotation = FreeCAD.Rotation(FreeCAD.Vector(1,0,0),-90)
    fcd08.ViewObject.ShapeColor = (1., 0., 0.) # RED
```

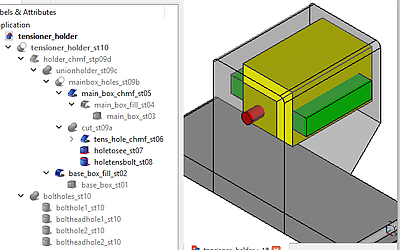
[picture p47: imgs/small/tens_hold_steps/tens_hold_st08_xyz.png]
Step 08

Step 08

Final hole:

Step 08

## Step 09: Fuse with the base and chamfer the unions:

```python
    #    --------------- step 09 --------------------------- 
    #    09a: Fuse all the elements to cut
    #    09b: Cut the box with the elements to cut
    #    09c: Fuse the base with the holder
    #    09d: chamfer the union
    #                             Z   Z
    #                             :   :
    #              _______        :   :____________
    #             /  ___  \       :   |  ._______ .|
    #             |:| O |:|       :   |::|_______| |...
    #            /| |___| |\      :   |  ..........|... tens_h/2 -tensnut_ap_tol
    #           / |_______| \     :   |            |  :+tens_pos_h
    #      ____/__|       |__\____:   |________   /   :  ...
    #  X..(_______|_______|_______)   |________|/.....:.....hold_bas_h
    #
    fcd09a = doc.addObject("Part::MultiFuse", 'cut_st09a')
    fcd09a.Shapes = [fcd06chmf, fcd07, fcd08]

    fcd09b = doc.addObject("Part::Cut", 'mainbox_holes_st09b')
    fcd09b.Base = fcd05
    fcd09b.Tool = fcd09a

    fcd09c = doc.addObject("Part::Fuse", 'unionholder_st09c')
    fcd09c.Base = fcd09b
    fcd09c.Tool = fcd02 #the base
    doc.recompute()

    # chamfer the union 09d
    chmf_rad = min(kidler.aluprof_w/2,
                   kidler.tens_pos_h + kidler.tens_h/2
                   - kidler.tensnut_ap_tol - kidler.hold_bas_h);
    edgechmf_list = []
    for edge_ind, edge in enumerate(fcd09c.Shape.Edges):
        if len(edge.Vertexes) == 2: #not all the edges have 2 vertexes
            v0 = edge.Vertexes[0]
            v1 = edge.Vertexes[1]
            # check if these 2 Vertexes have Z = kidler.hold_bas_h
            # and if the X is either aluprof_w or aluprof_w + hold_w
            if ( abs(v0.Z -kidler.hold_bas_h) < mindif and
                 abs(v1.Z -kidler.hold_bas_h) < mindif and
                ((( abs(v0.X -kidler.aluprof_w) < mindif) and
                  ( abs(v1.X -kidler.aluprof_w) < mindif)) or
                 (( abs(v0.X -(kidler.aluprof_w+kidler.hold_w)) < mindif) and
                  ( abs(v1.X -(kidler.aluprof_w+kidler.hold_w)) < mindif)))):
                edgechmf_list.append((edge_ind+1, chmf_rad, chmf_rad))
    fcd09d = doc.addObject ("Part::Chamfer", 'holder_chmf_stp09d')
    fcd09d.Base = fcd09c
    fcd09d.Edges = edgechmf_list
    doc.recompute()
    # hide the step 09c:
    fcd09c.ViewObject.Visibility = False
```

Step 09  
Step 09

## Step 10: Bolt holes to attach the piece to the aluminum profile
```python
   #    --------------- step 10 --------------------------- 
    #    Bolt holes to attach the piece to the aluminum profile
    #                              Z   Z
    #                              :   :
    #               _______        :   :____________
    #              /  ___  \       :   |  ._______ .|
    #              |:| O |:|       :   |::|_______| |
    #             /| |___| |\      :   |  ..........|
    #            / |_______| \     :   |            |
    #       ____/__|       |__\____:   |________   /
    #   X..(__::___|_______|__::___)   |___::___|/
    #
    fcd10_shank1 =  doc.addObject("Part::Cylinder",'bolthole1_st10')
    fcd10_shank1.Radius = kidler.boltaluprof_r_tol
    fcd10_shank1.Height = kidler.hold_bas_h + 2.
    fcd10_shank1.Placement.Base = FreeCAD.Vector(kidler.aluprof_w/2.,
                                                 kidler.aluprof_w/2.,
                                                 -1) 
    fcd10_head1 =  doc.addObject("Part::Cylinder",'boltheadhole1_st10')
    fcd10_head1.Radius = kidler.boltaluprof_head_r_tol
    fcd10_head1.Height = kidler.boltaluprof_head_l
    fcd10_head1.Placement.Base = FreeCAD.Vector(kidler.aluprof_w/2.,
                                                kidler.aluprof_w/2.,
                                                kidler.hold_bas_h) 
    fcd10_shank2 =  doc.addObject("Part::Cylinder",'bolthole2_st10')
    fcd10_shank2.Radius = kidler.boltaluprof_r_tol
    fcd10_shank2.Height = kidler.hold_bas_h + 2.
    fcd10_shank2.Placement.Base = FreeCAD.Vector(
                                        kidler.hold_bas_w-kidler.aluprof_w/2.,
                                        kidler.aluprof_w/2.,
                                        -1) 
    fcd10_head2 =  doc.addObject("Part::Cylinder",'boltheadhole2_st10')
    fcd10_head2.Radius = kidler.boltaluprof_head_r_tol
    fcd10_head2.Height = kidler.boltaluprof_head_l
    fcd10_head2.Placement.Base = FreeCAD.Vector(
                                        kidler.hold_bas_w-kidler.aluprof_w/2.,
                                        kidler.aluprof_w/2.,
                                        kidler.hold_bas_h) 
    # fusion of all the bolts and heads
    fcd10_bholes = doc.addObject("Part::MultiFuse", 'boltholes_st10')
    fcd10_bholes.Shapes = [fcd10_shank1, fcd10_head1, fcd10_shank2, fcd10_head2]
    doc.recompute()
    # change color to light orange:
    fcd10_bholes.ViewObject.ShapeColor = (1., 0.5, 0.0)

    fcd10_final = doc.addObject("Part::Cut", 'tensioner_holder_st10')
    fcd10_final.Base = fcd09d # the holder (without the profile bolt holes)
    fcd10_final.Tool = fcd10_bholes # bolt holes
    doc.recompute()
    return fcd10_final

```
step10bolts   
step10bolts

Final cut:

Tensioner holder

## Step 11: Saving, rotating to print and export:

```python

# creation of a new FreeCAD document
doc = FreeCAD.newDocument()
# creation of the tensioner holder
fcd_tens_holder = tensioner_holder()
# change color to light sky blue:
fcd_tens_holder.ViewObject.ShapeColor = (0.5, 0.7, 1.0)

# ---------- export to stl
stlPath = filepath + '/../stl/'
stlFileName = stlPath + 'tensioner_holder' + '.stl'
# rotate to print without support:
fcd_tens_holder.Placement.Rotation = (
                    FreeCAD.Rotation(FreeCAD.Vector(1,0,0), 90))
# exportStl is not working well with FreeCAD 0.17 (worked on 0.16 and 0.15)
#fcd_tens_holder.Shape.exportStl(stlFileName)
mesh_shp = MeshPart.meshFromShape(fcd_tens_holder.Shape,
                                  LinearDeflection=kparts.LIN_DEFL, 
                                  AngularDeflection=kparts.ANG_DEFL)
mesh_shp.write(stlFileName)
del mesh_shp

# rotate back, to see it in its real position
fcd_tens_holder.Placement.Rotation = (
                    FreeCAD.Rotation(FreeCAD.Vector(1,0,0), 0))

# save the FreeCAD file
freecadPath = filepath + '/../freecad/'
freecadFileName = freecadPath + 'tensioner_holder' + '.FCStd'
doc.saveAs (freecadFileName)

```

Tensioner holder rotated to be exported to stl and print:

Tensioner holder

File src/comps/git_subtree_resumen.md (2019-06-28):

# Estructura de subtree para los scripts de Python para diseños FreeCad

En este ejemplo vamos a ver cómo integrar el módulo `comps` de python en otros módulos que lo usen.

La mayor parte de la información se ha obtenido de aquí:
https://andrey.nering.com.br/2016/git-submodules-vs-subtrees/

Aquí también hay info, pero me gusta más la de arriba:

https://medium.com/@porteneuve/mastering-git-subtrees-943d29a798ec

Resumen de la estructura que tengo en mi ordenador local, queremos hacer algo parecido en nuestro ordenador local:

```
py_freecad/              # python scripts for FreeCAD
  +-- comps/               # library of components
      +-- comps.py            # components
      +-- kcomp.py            # constants about components
      +-- fcfun.py            # library of functions
  +-- citometro/          # citometer scripts
      +-- epi3.py         # Utiliza comps
      +-- modules/        # ------ subtree del comps
          +-- comps/
              +-- comps.py
              +-- kcomp.py
              +-- fcfun.py
  +-- freecad_filter_stage/   
      +-- src/
          +-- filter_holder_clss.py  # Utiliza comps
          +-- comps/      # ------ subtree del comps
```

Vamos a crear un nuevo repositorio `mi_pyfcad`, que también use el `comps`.
Lo primero es tener el repositorio `comps` en local. Lo bajamos de internet. Vamos a la carpeta raiz donde lo queremos:

```
py_freecad $ git clone https://github.com/felipe-m/fcad-comps.git comps
```

Ponemos el `comps` al final para que el nombre sea `comps` y no `fcad-comps` que es el nombre que está en el github.

Con esto tenemos todo el módulo `comps` dentro del directorio `py_freecad`
```
py_freecad/              # python scripts for FreeCAD
  +-- comps/               # library of components
      +-- .git/               # carpeta del repositorio git
      +-- comps.py            # components
      +-- kcomp.py            # constants about components
      +-- fcfun.py            # library of functions
      +-- ....
```

Ahora vamos a crear un repositorio que use el módulo `comps`. Lo llamaremos `mi_pyfcad`:

```
py_freecad $ mkdir mi_pyfcad
py_freecad $ cd mi_pyfcad
py_freecad/mi_pyfcad $ git init
```

Ahora ya podemos crear los ficheros. Los podemos crear directamente, o si queremos, los creamos en un directorio de ficheros fuente (src). Vamos a crearlo en un directorio de ficheros fuente:

```
py_freecad/mi_pyfcad (master) $ mkdir src
py_freecad/mi_pyfcad (master) $ cd src
```

En este directorio creamos nuestros ficheros python.
Por ejemplo, vamos a suponer que creamos un fichero `prueba.py` que usa una función de `comps/comps.py`.

Como este fichero `prueba.py` va a utilizar funciones de `comps/comps.py`, al principio tendrá la siguiente sentencia para añadir el path de comps:

```
sys.path.append(filepath + '/../../' + 'comps'
```

Lo que hace esta sentencia es añadir el camino relativo desde `py_freecad/mi_pyfcad/src` a `py_freecad/comps`, es decir
* subir (o bajar, según se mire) de `src` a `mi_pyfcad`
* y de `mi_pyfcad` a `py_freecad`,
* y luego bajar (o subir) a `comps`

Volvemos al directorio raíz de `mi_pyfcad` y hacemos un primer _commit_:

```
py_freecad/mi_pyfcad/src (master) $ cd ..
py_freecad/mi_pyfcad (master) $ git add .
py_freecad/mi_pyfcad (master) $ git commit -m "Initial commit"
```

La estructura que tenemos será:

```
py_freecad/              # python scripts for FreeCAD
  +-- comps/               # library of components
      +-- .git/               # carpeta del repositorio git
      +-- comps.py            # components
      +-- kcomp.py            # constants about components
      +-- fcfun.py            # library of functions
      +-- ....
  +-- mi_pyfcad/
      +-- .git/               # carpeta del repositorio git
      +-- src/
          +--prueba.py        # este fichero usa funciones de ../../comps
```

Tal como lo tenemos ahora, podemos hacer cambios en los ficheros de `mi_pyfcad` y usar las funciones de `comps`.
**Podríamos trabajar así sin problema**.

Sin embargo, podríamos querer tener un _subtree_ de `comps` dentro del repositorio `mi_pyfcad`.
Dos razones que se me ocurren:
* Por mantener sincronizado lo que funciona de `mi_pyfcad` junto con la versión que funciona de `comps`. Es decir, tener una versión conjunta de lo que funciona. Por si quiero volver atrás a una versión anterior de ambos, que conjuntamente funcionen.
* Por necesitar probar cambios en `comps` sin modificar la versión original hasta que los pruebe.

En este caso, puedo hacer un _subtree_:

**Añadimos `comps` como remoto**:

```
py_freecad/mi_pyfcad (master) $ git remote add comps ../comps
```

En el `remote add` se pone `comps` no el camino donde se va a guardar porque es sólo el nombre.
Que puedo verlo. Es un remoto local (no un remoto de github):

```
py_freecad/mi_pyfcad (master) $ git remote -v
comps    ../comps (fetch)
comps    ../comps (push)
```

Ahora añado el _subtree_, que aquí si que pongo el camino donde va a ir, por ejemplo:

```
py_freecad/mi_pyfcad (master) $ git subtree add --squash --prefix=src/comps/ comps master
```

Con esto, se ha creado/copiado todo el directorio comps dentro de src/comps/

```
py_freecad/              # python scripts for FreeCAD
  +-- comps/               # library of components
      +-- .git/               # carpeta del repositorio git
      +-- comps.py            # components
      +-- kcomp.py            # constants about components
      +-- fcfun.py            # library of functions
      +-- ....
  +-- mi_pyfcad/
      +-- .git/               # carpeta del repositorio git
      +-- src/
          +--prueba.py        # este fichero usa funciones de ../../comps
          +-- comps/          # esta es copia del repositorio comps
              +-- comps.py            # components
              +-- kcomp.py            # constants about components
              +-- fcfun.py            # library of functions
              +-- ....
```

Con esto se ha copiado/comprimido (squashed) toda la historia del comps en `mi_pyfcad`

Si quisiese utilizar los ficheros del comps locales, dentro de mi repositorio, debería cambiar el camino (path) en nuestro fichero `prueba.py`:

```
sys.path.append(filepath + '/' + 'comps'
```

Con esto, ya podemos hacer los cambios que hagamos en `comps` local dentro de `mi_pyfcad`

Para actualizar cambios futuros, no se hace `subtree add`, sino `subtree pull`. Sin embargo, es mejor primero hacer commit de todos los cambios de este directorio y luego añadir los cambios del comps
```
py_freecad/mi_pyfcad (master) $ git subtree pull --squash --prefix=src/comps/ comps master
```

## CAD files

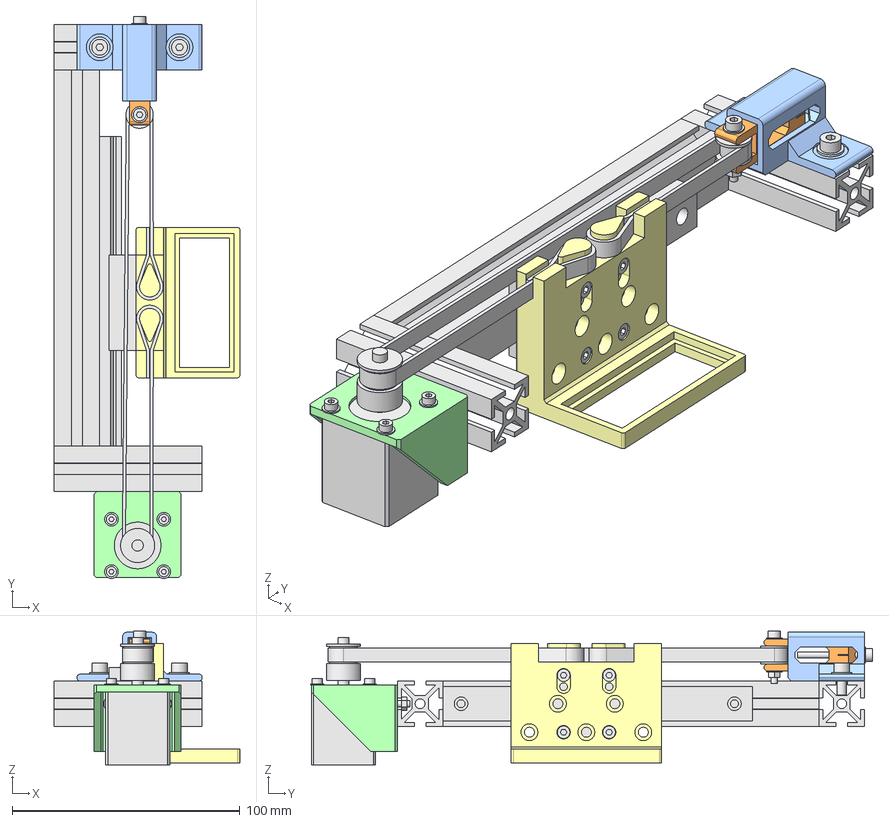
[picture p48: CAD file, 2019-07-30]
freecad/filter_stage.FCStd
81.5 x 246.7 x 58.8 mm
filter_holder
NB_SEB15A_block
filter_bolt_w_2_d_1
filter_bolt_w_2_d1
filter_bolt_w2_d_1
filter_bolt_w2_d1
NB_SEB15A
bearing_idlpulley_m3
idler_tensioner
d912bolt_washer_m3
d9343
leadscrew_nut
tensioner_holder
d912bolt_washer_m3001
aluprof_w20l_65
d912bolt_washer_m4
d912bolt_washer_m4001
nema11_pulley_set
nema11_motorholder
motor_bolt_w_2_d2
motor_bolt_w_2_d4
motor_bolt_w2_d2
motor_bolt_w2_d4
aluprof_w20l_65001
d912bolt_washer_m3002
d934nut_m3001
d912bolt_washer_m3003
d934nut_m3002
aluprof_w20l_165
gt2_belt

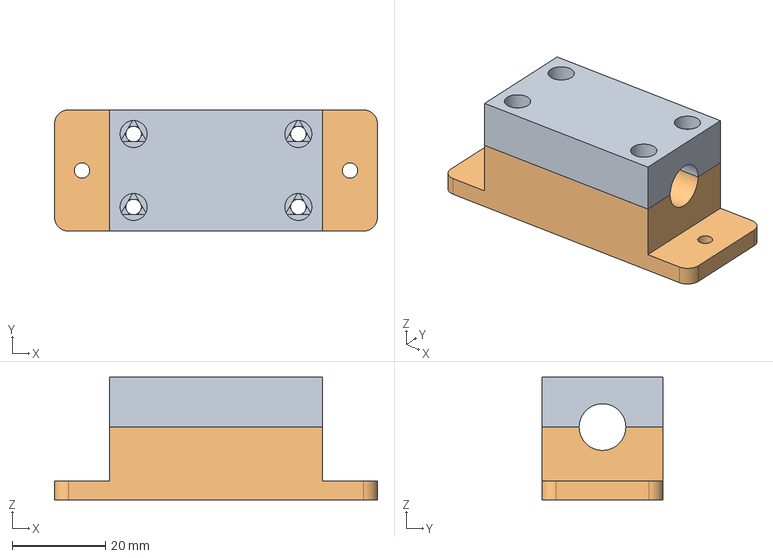
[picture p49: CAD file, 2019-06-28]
src/comps/freecad/thinlinbearhouse1rail_lm8mm.FCStd
69.3 x 26.0 x 26.3 mm
thinlinbearhouse1rail_lm8_top
thinlinbearhouse1rail_lm8_bot

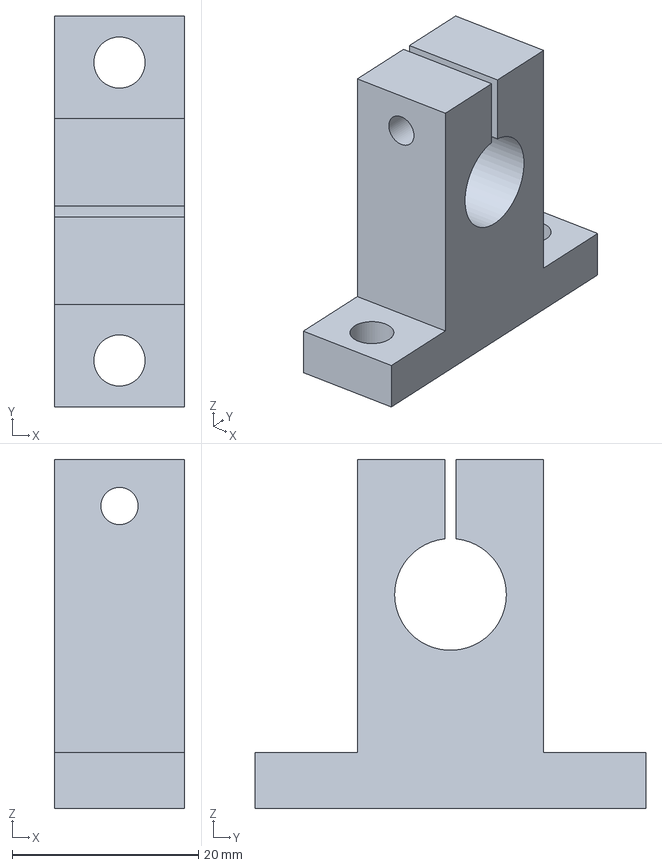
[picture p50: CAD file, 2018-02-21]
src/comps/step/sk12.step
14.0 x 42.0 x 37.5 mm

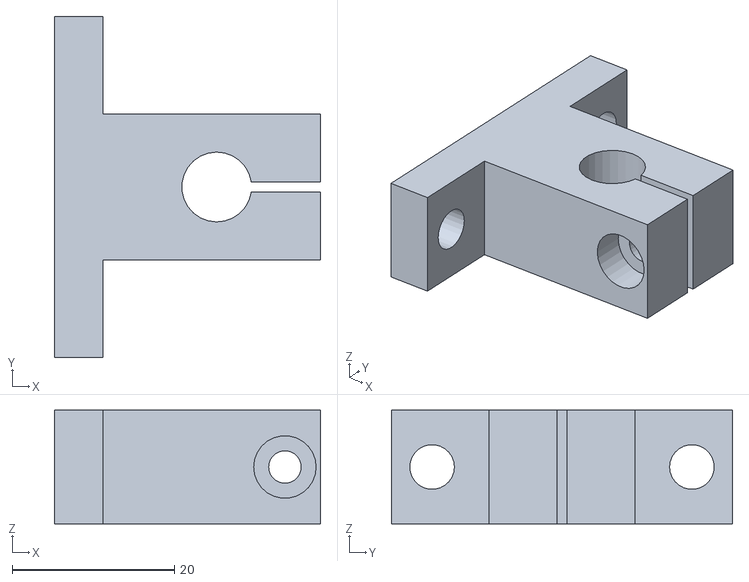
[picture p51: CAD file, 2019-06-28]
src/comps/stl/sk8_tol03.stl
32.8 x 42.0 x 14.0

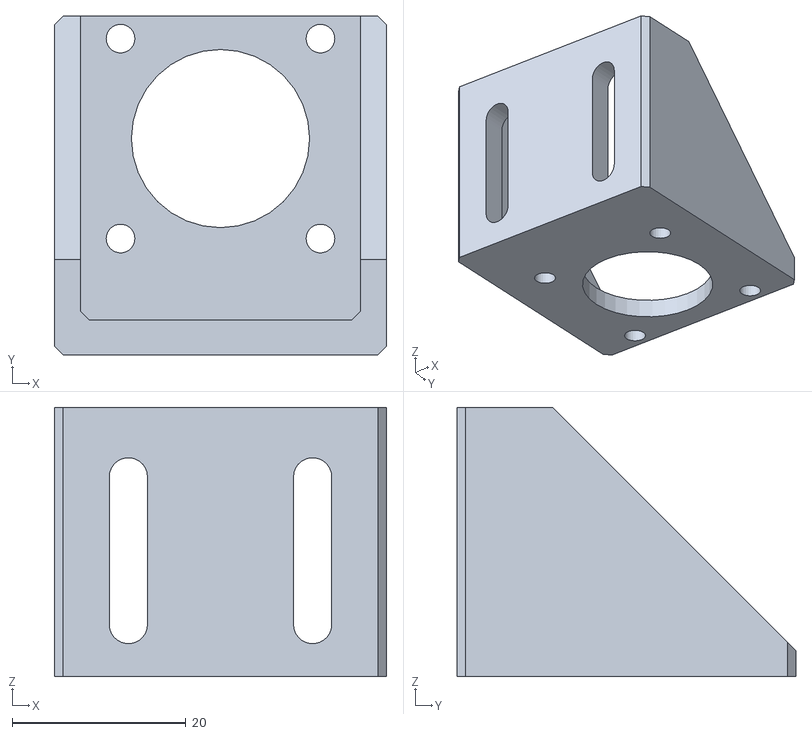
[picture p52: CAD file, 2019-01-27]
stl/motor_holder.stl
38.2 x 39.0 x 31.0

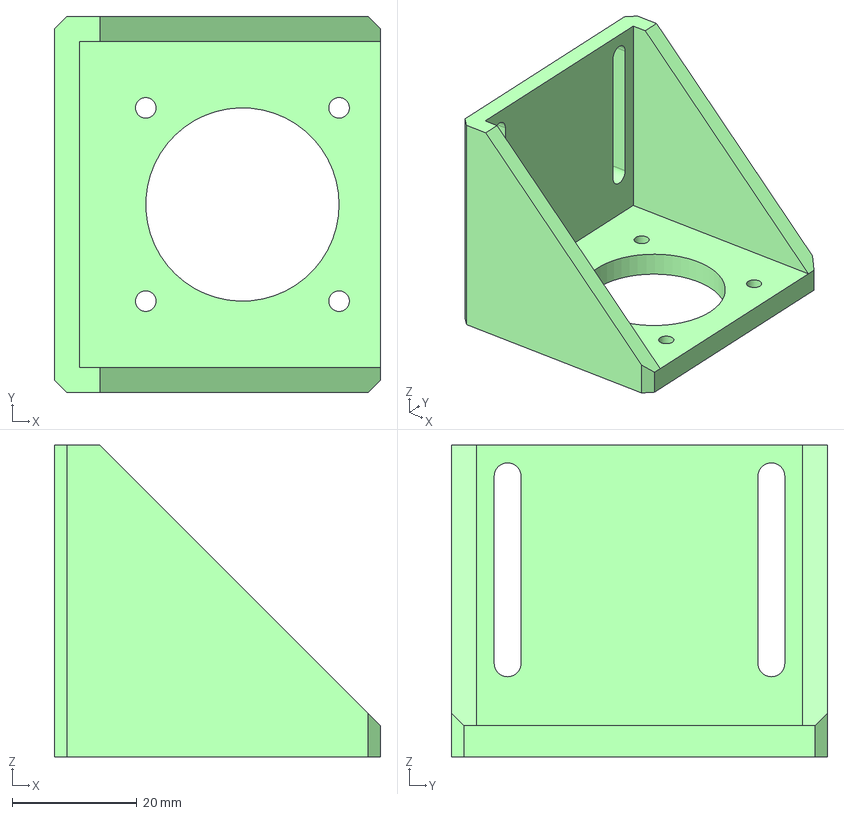
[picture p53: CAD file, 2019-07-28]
freecad/simpler_motor_holder.FCStd
52.3 x 60.3 x 50.0 mm

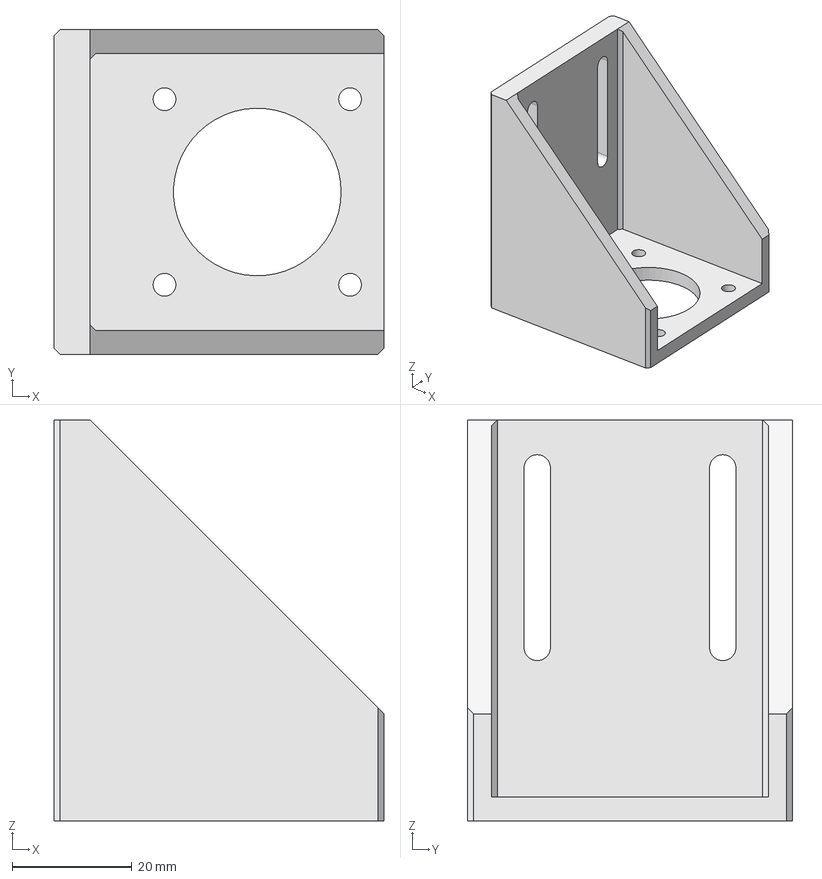
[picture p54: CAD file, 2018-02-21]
src/comps/step/nema17holder_25_55.step
55.1 x 54.3 x 67.0 mm

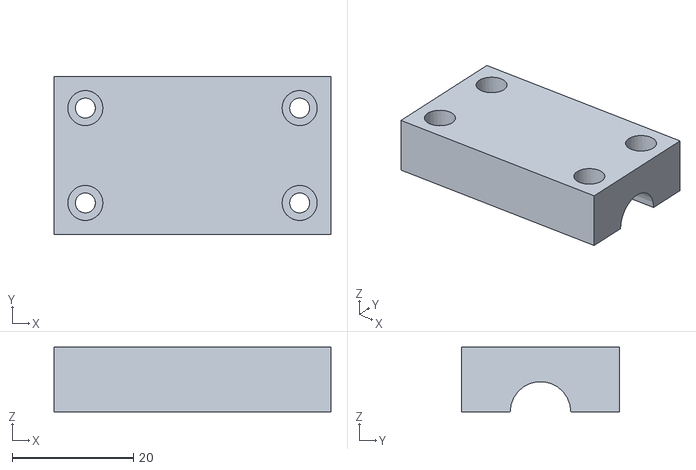
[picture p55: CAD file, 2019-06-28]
src/comps/stl/thilinbearhouse1rail_lm8_top.stl
45.7 x 26.0 x 10.7

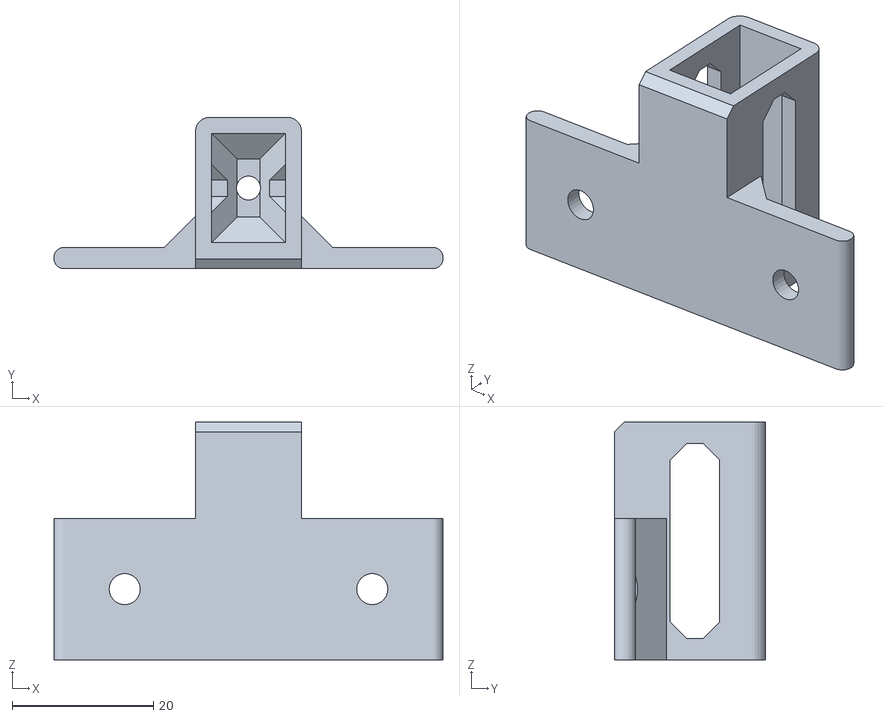
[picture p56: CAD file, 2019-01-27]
stl/class_tensioner_holder.stl
55.0 x 21.4 x 33.6

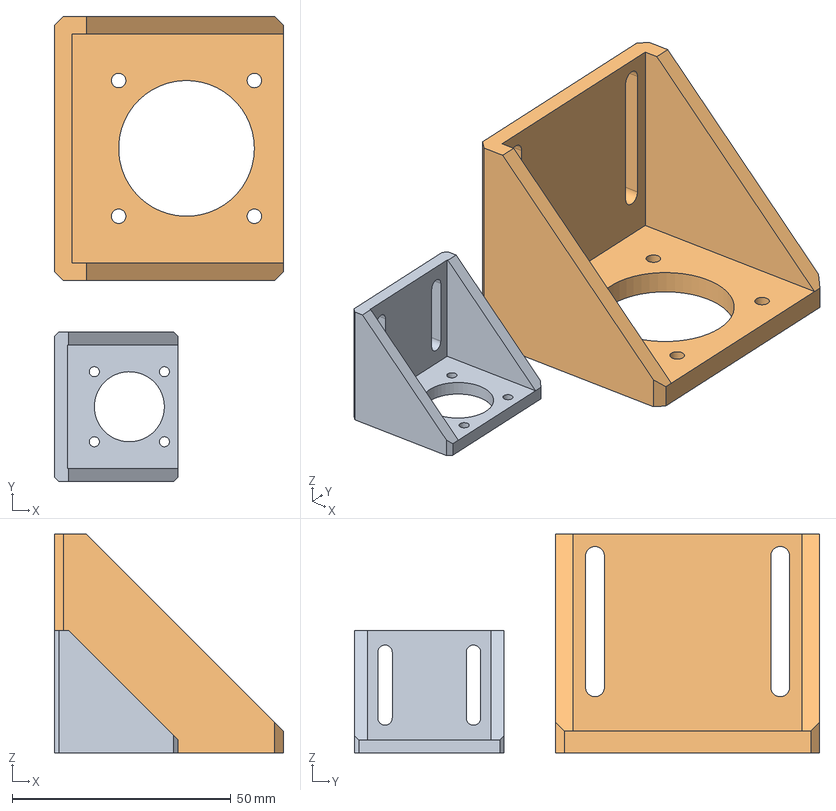
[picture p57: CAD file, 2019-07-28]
freecad/simpler_motor_holder_2sizes.FCStd
52.3 x 106.2 x 50.0 mm
step06
step06001

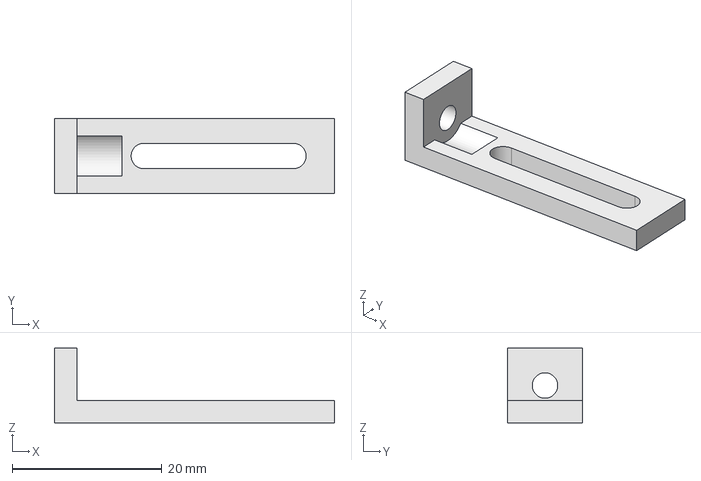
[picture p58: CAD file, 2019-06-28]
src/comps/freecad/bracket10_m3perplin_rail20_noreinfore.FCStd
37.5 x 10.0 x 10.0 mm

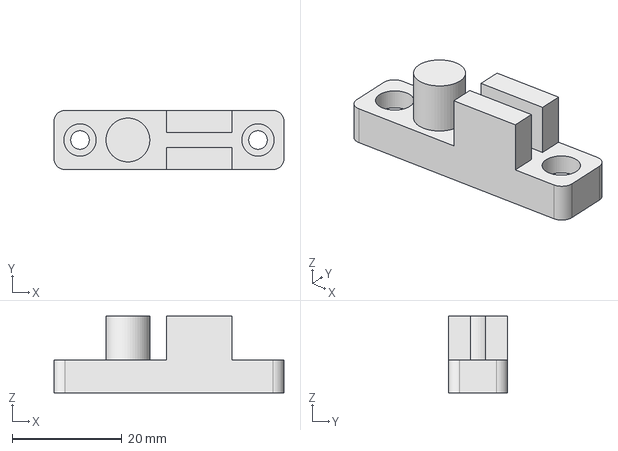
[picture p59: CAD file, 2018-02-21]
src/comps/step/beltclamp_m3.step
42.0 x 10.8 x 14.0 mm

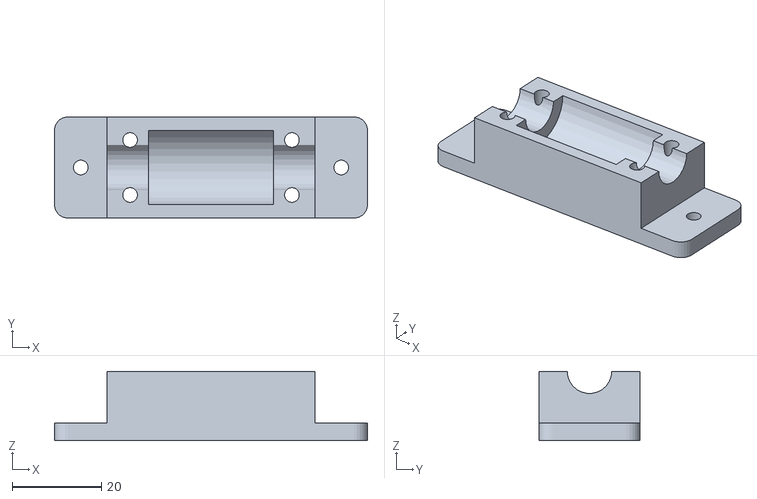
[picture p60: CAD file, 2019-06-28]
src/comps/stl/thilinbearhouse1rail_8mm_bot.stl
70.3 x 22.7 x 15.6

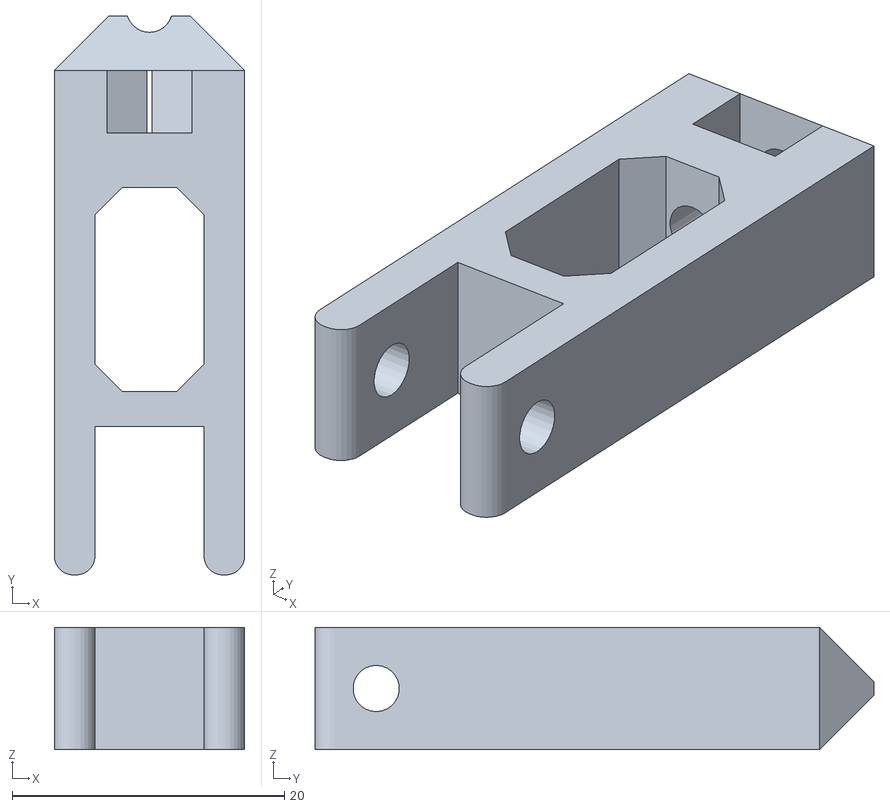
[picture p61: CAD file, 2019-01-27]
stl/class_idler_tensioner.stl
14.0 x 41.1 x 9.00

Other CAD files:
src/comps/freecad/sk6_tol03.FCStd
freecad/filter_stage_printable_parts.FCStd
src/comps/freecad/makerbeam_xl15_200.FCStd
src/comps/stl/thinlinbearhouse1rail_lm8_tol04xtrshank_bot.stl
freecad/filter_holder.FCStd
freecad/filter_holder_2sizes.FCStd
freecad/filter_holder_draw.FCStd
freecad/filter_holder_linguide_belt.FCStd
freecad/filter_holder_linguide_belt_cut.FCStd
freecad/filter_holder_linguide_beltcut_exploded.FCStd
freecad/filter_holder_linguide_exploded.FCStd
freecad/filter_stage_30.FCStd
freecad/filter_stage_n30.FCStd
freecad/filter_stage_smprof.FCStd
freecad/idler_tensioner.FCStd
freecad/idler_tensioner_3strokes.FCStd
freecad/idler_tensioner_3strokes_drawing.FCStd
freecad/idler_tensioner_draw.FCStd
freecad/idlerpulley_2leadscrewmtr.FCStd
freecad/idlerpulley_2wallthick.FCStd
freecad/idlerpulley_bearwash.FCStd
freecad/ilder_tensioner.FCStd
freecad/tens_holder_ex_2idlertens.FCStd
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

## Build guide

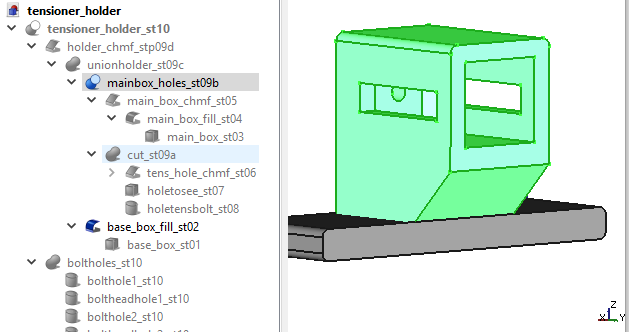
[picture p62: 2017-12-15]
imgs/tens_hold_steps/tens_hold_st08_xyz_final.png

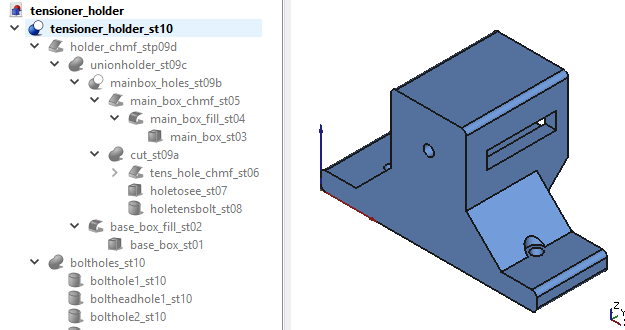
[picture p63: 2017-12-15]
imgs/tens_hold_steps/tens_hold_st10_final.png

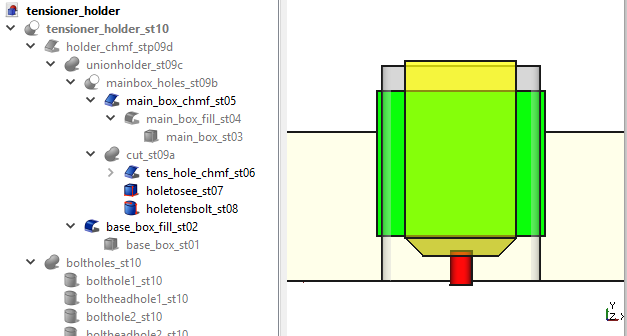
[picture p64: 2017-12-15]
imgs/tens_hold_steps/tens_hold_st08_xy.png

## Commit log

2017-12-15 Squashed 'src/comps/' content from commit 307d310
    git-subtree-dir: src/comps
    git-subtree-split: 307d310bcd7b0fb3186b621c3dee35793a44c178
    [linfiltersup.FCStd, linfiltersup_fix.stl, linfiltersup_mov.stl, xend_shaft_slider.FCStd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]
2017-12-16 Change variable name
    belt_pos_h -> gt2_pos_h
    aluprof_bolt_d -> boltaluprof_d
2017-12-29 Add export to STL and tensioner_set documentation
    [idler_tensioner.FCStd, idler_tensioner.stl, set_idler_tensioner.stl, set_tensioner_holder.stl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]
2018-01-14 Squashed 'src/comps/' changes from 48bd19f..ff3dcc5
    ff3dcc5 Add placement dependencies
    bc4b301 Place SingleParts and parts inside PartsSet objets
    65316b9 Change name of class: from TopoShp to Obj3D
    b6e1a1b Add BearWashSet class and methods to get position
    86ecf32 Add BearingOutl class
    8915ee5 New class structure
    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
2018-02-11 Add draft of filter_holder_clss.py
    Not finished yet, just the beginning
2018-02-18 Add unfinished version of filter_holder_clss.py
2018-02-18 Continue with filter_holder_class
    Only belt clamps are left
2018-02-18 Add working version of filter_holder_clss.py
    [filter_holder.FCStd]
2018-02-21 Add filter stage model
    In this file src/filter_stage.py, first version
    Motor holder is still needed
2018-02-21 Squashed 'src/comps/' changes from ff3dcc5..290461a
    290461a Fix bug in fc_class function: place_fcos
    07332b3 Add 3 freecad generated models
    00ff2bd Add condition of Edge with 2 vertexes
    80232aa Add file to generate electric components
    cd7f8d3 Add argument to shp_cableturn to have extra length
    97cc51f Change what happens when no coordinate vector
    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
    [belt_clamp_tensioner.stl, beltclamp_m3.FCStd, beltclamp_m3.step, beltclamp_m3.stl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]
2018-02-21 Add motor holder to filter stage
    src/filter_stage.py
    [filter_stage.FCStd]
2018-04-05 Fix bug in the hole for the tensioner nut
    The dimmension was the radius of the leadscrew, and it
    should be the circumradius of the nut (tolerance added)
    [tensioner_set_aluprof20_h17_strk10.FCStd]
2018-04-09 Add extra tolerance to the holder
    [tensioner_set_aluprof20_h17_strk10_xtrtolholder.FCStd]
2018-04-11 Add 0.6mm tolerance for the tensioner hold
    It seems that the printer is leaving a lot of material, so
    more tolerance is needed
    [tensioner_set_aluprof20_h17_strk10_xtrtol06holder.FCStd]
2018-04-11 Fix bug: dimension of the tensionr nut hole
    It was not the circumradius but just the inner radius
    [idler_tensioner.FCStd, idler_tensioner.stl, set_idler_tensioner.stl, tensioner_set.FCStd]
2018-04-12 Add more tolerance to the tensioner holder: 0,7mm
    at each side. The printer is not working well
    [tensioner_set_aluprof20_h17_strk10_xtrtol07holder.FCStd]
2018-04-25 Add freecad variation h belt 22.5
    [tensioner_set_aluprof20_h22_5_strk10_xtrtol07holder.FCStd]
2018-04-25 Add freecad model with h belt center at 32.5
    [tensioner_set_aluprof20_h32_5_strk10_xtrtol07holder.FCStd]
2018-04-30 Add 2 tensioner holders freecad models
    with differente heights
    [tensioner_set_aluprof20_h37_5_strk10_xtrtol07holder.FCStd, tensioner_set_aluprof20_h47_5_strk10_xtrtol07holder.FCStd]
2018-06-06 Add option of minimun width for the rim
    [tensioner_set_aluprof20_h12_5_strk10_xtrtol07holder_minwidth.FCStd]
2018-06-06 Correct rim chamfer dimensions
    [tensioner_set_aluprof20_h15_strk10_xtrtol07holder_minwidth.FCStd]
2018-07-12 Squashed 'src/comps/' changes from 290461a..a3e60a6
    a3e60a6 Fix bug in kcomp.py in linearbearing housing
    b047b2d Add Nema holder 52mm total height
    f3ab5f1 Add 4 new sizes for Ilder pulley holder freecad
    1d79e5c Add motor holder with m3 diameter wall bolts
    bc454cf Add option to not have a rail in nema holder
    e86812e Add a motor new holder with 8-38 rail
    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
    [dc_motor_turn_135_2.FCStd, idler_pulley_holder_31_above_h.FCStd, idler_pulley_holder_34_above_h.FCStd, idler_pulley_holder_41_above_h.FCStd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]
2018-07-13 Update to FreeCAD version 0.17
    exportStl is not working properly
    [idler_tensioner.FCStd, idler_tensioner.stl, set_idler_tensioner.stl, set_tensioner_holder.stl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]
2018-07-13 Squashed 'src/comps/' changes from a3e60a6..8916a7a
    8916a7a Update to FreeCAD 0.17
    git-subtree-split: 8916a7a430efa78f774cd790a6e82fb649c428cc
    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
    [linbearhouse__sc10uu_bot.stl, linbearhouse_sc10_uu_top.stl]
2018-07-26 Add pulley and new motor holder
2018-07-26 Add the new version of the nema Motor
2018-07-27 Squashed 'src/comps/' changes from 8916a7a..d2b3dc0
    d2b3dc0 Move class NemaMotorPulleySet partset.py
    92c8404 Add NemaMotorPulleySet
    5acdf3a Add a Obj3D and SinglePart class version of the Nema motor
    45a20c4 Add PartNemaMotorHolder
    d97f553 Add ShpNemaMotorHolder
    0fe2d33 Add GT2 Pulley part
    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
2018-08-01 Switch to partset.NemaMotorPulleySet
    Instead of creating the Motor and Pulley separately
2018-08-01 Add NemaMotorPulleyHolderSet
    instead of using the holder and the motor with pulley separately
2018-08-07 Align the elements (in progress)
    [filter_stage.FCStd]
2018-08-08 Set elements independent of filter position
    [filter_stage.FCStd]
2018-08-09 Rearrangement of the elements
    [filter_stage.FCStd]
2018-08-09 Include the aluminum profile for linear guide
    [filter_stage.FCStd]
2018-08-15 Fix some bugs, the belt seems to work
    [filter_stage.FCStd]
2018-08-15 Different versions of the filter stage
    [filter_stage.FCStd, filter_stage_30.FCStd, filter_stage_n30.FCStd]
2018-08-18 Fix the bug of the nut holes of the images
    It was already fixed in the python scripts, but not the images
    [filter_stage_smprof.FCStd, idler_tensioner.FCStd]
2018-08-18 Add filter stage image
2018-08-20 Update tensioner class
    [tensioner_set.FCStd]
2018-08-22 Add a bolt for the idler pulley
    [idler_tensioner.FCStd, tensioner_holder.FCStd, tensioner_set.FCStd]
2018-08-22 Add bolt for tensioner leadscrew
2018-08-22 Add washers to pulley bolt
    [filter_stage.FCStd]
2018-08-23 Add leadscrew nut of tensioner
2018-08-23 Add nut for the pulley bolt
2018-08-24 Add the washer to the tensioner bolt
    [filter_stage.FCStd, tensioner_set.FCStd]
2018-08-24 Fix bug related to the tensioner leadscrew length
    [tensioner_holder.FCStd]
2018-08-24 Add tensioner with different extensions to compare
    [filter_stage.FCStd, tensioner_holder_2_extend.FCStd, tensioner_holder_2_extend_side.FCStd]
2018-09-01 Add some variations of the models and bolts
    to the filter holder
    [filter_holder_linguide_belt.FCStd, filter_holder_linguide_belt_cut.FCStd, filter_holder_linguide_beltcut_exploded.FCStd, filter_holder_linguide_exploded.FCStd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]
2018-09-01 Fix bug calling BearWashSet, used a wrong bolt
2018-09-02 Add bolts to stage and examples
    [filter_stage.FCStd, idlerpulley_2leadscrewmtr.FCStd, idlerpulley_2wallthick.FCStd, idlerpulley_bearwash.FCStd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]
2018-09-02 Add bolts to belt tensioners
    [tens_holder_ex_3profiles.FCStd]
2018-09-02 Add filter holder examples
    [filter_holder_2sizes.FCStd, filter_holder_draw.FCStd]
2019-01-26 Add more documentation and image files
    [filter_holder_2sizes.FCStd]
2019-01-27 Improve documentation and add some STL files
    [filter_holder.stl, filter_stage_printable_parts.FCStd, idler_tensioner_example.stl, motor_holder.stl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]
2019-01-27 Add readme for STL directory
    [class_idler_tensioner.stl, class_tensioner_holder.stl]
2019-06-28 Squashed 'src/comps/' changes from d2b3dc0..65dff90
    65dff90 Add tolerances to simplendstopholder nut hole
    071c22a Add a new endstop with holes not aligned
    7464126 Add extra tol to shank
    35184ed Merge pull request #1 from davidmubernal/master
    a0b24cf Fix bug
    b340184 Add tolerances for thinlinbearhouse1rail bolts
    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
    [bracket10_m3perp_m4lin_rail25_noreinfore.FCStd, bracket10_m3perp_m4lin_rail25_noreinfore.stl, bracket10_m3perplin_rail20_noreinfore.FCStd, bracket10_m3perplin_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]
2019-06-28 Squashed 'src/comps/' changes from 65dff90..3ff3397
    3ff3397 Add CNY70 and TCRT5000L optical sensor holder
    e654adc Merge pull request #2 from davidmubernal/master
    e563eaa Fix Bug FreeCAD 0.18
    git-subtree-split: 3ff3397e1f89d4dbc3e7ad94fe1080bb265c88b3
    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
2019-07-27 Remove filter_holder.py
    It was an old version
2019-07-27 Add a simpler script for the nema motor holder
2019-07-28 Add bolts to the motor
    Change prints to python 3
    [filter_holder.stl, simpler_motor_holder.FCStd, simpler_motor_holder_2sizes.FCStd]
2019-07-28 Add bolts to attach the motor holder to the profile
    [filter_stage.FCStd]
2019-07-29 Add washers to the motor bolts
    [filter_stage.FCStd]
2019-07-30 Add nuts to the filter stage motor bracket
    [filter_stage.FCStd]
2019-10-08 Add cadquery versions
    Filter holder not finished
2019-10-08 Improved version of filter_holder for cadquery
    Still some error
2019-10-09 Working version of filter holder
